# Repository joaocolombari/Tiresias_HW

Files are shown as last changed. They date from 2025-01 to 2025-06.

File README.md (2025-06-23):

<div align="center">
  <h1>Tiresias Hardware</h1>
   <p>Altium Designer Hardware files for the Tiresias Hearing Aid project </p>
</div>

<p align="center">
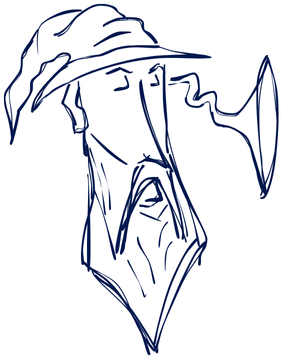
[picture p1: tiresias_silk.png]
  
</p>

<div align="center">
  
  
  
</div>

## Introduction

This repository contains the Altium Designer Project for the Tiresias Hearing Aid Development Board. 

The Tiresias project is part a partnership between the Brazilian Schools [FOB-USP](https://www1.fob.usp.br) and [EESC-USP](https://www.eesc.usp.br/) aiming to adress some of the Brazilian healthcare system's demands. Conduced by the [GMETA](https://sel.eesc.usp.br/jcarmo/metamaterials/) R&D Group, it aims to develop an open-source national technology for hearing aid applications using off-the-shelf components.

Tiresias is a low-power, resource-constrained open-source development board for hearing aid prototyping. It integrates an easy-to-program audio codec supporting both standard hearing aid functions — such as nonlinear amplitude compression and multichannel filtering — and advanced processing techniques, including adaptive filtering and beamforming for noise reduction and speech enhancement.

## System Architecture

### Key Features

- **Advanced Signal Processing**
  - Multichannel compression for improved speech intelligibility
  - Adaptive microphone directivity (beamforming, cardioid)
  - Noise reduction using directional microphone arrays

- **Wireless Connectivity & IoT Integration**
  - Bluetooth LE Audio (BT 5.4) with LC3 codec support
  - Isochronous Channels for synchronized, low-latency audio streaming
  - Support for binaural and Auracast™ systems
  - Remote configuration and smartphone/device interaction

- **Sensor Integration**
  - Voice Pick-Up Units (VPU): Bone-conduction speech capture for noisy environments
  - MEMS Microphones: Multi-microphone, low-power setups
  - Inertial Measurement Units (IMUs): Head tracking, ExG augmentation, fall detection, and health monitoring

- **Power Management**
  - Support for rechargeable Li-Po batteries
  - Power Management ICs (PMICs) for voltage regulation and safe charging

### Hardware overview

The project uses a [nRF5340 SoC](https://www.nordicsemi.com/Products/nRF5340) from [Nordic Semiconductors](https://www.nordicsemi.com). It contains an **application proccessor** for handling the main functions and a dedicated **network processor** for handling Bluetooth Low Energy (BLE) connectivity. Moreover, the design integrates:

- **[ADAU1787 Audio Codec](https://www.analog.com/en/products/adau1787.html)**  audio codec from [Analog Devices](https://www.analog.com/en/index.html) with integrated digital signal processing (DSP) instructions for real-time signal processing;
- Onboard **Nordic [nPM1100 PMIC](https://www.nordicsemi.com/Products/nPM1100)** battery management system for portable operation;
-  **Multiple [AMM-3742-T-WP-R MEMS microphones](https://puiaudio.com/product/microphones/amm-3742-t-wp-r)** from [PUI Audio](https://puiaudio.com/) for beamforming and noise reduction applications;
-  **[V2S200D](https://www.mouser.com/datasheet/2/218/v2s200d_user_guide-3179748.pdf) Digital Voice Vibration Sensor** from [Knowless](https://www.knowles.com/) for self-speech recognition and adaptation; 
-  **[BMI270[(https://www.bosch-sensortec.com/products/motion-sensors/imus/bmi270/) Inertial Measurement Unit** from [Bosch](https://www.bosch-sensortec.com/) for motion and physiological data monitoring;
-  **[MX25R1635](https://www.mxic.com.tw/zh-tw/flash-memory-solutions/automotive/Pages/spec.aspx?p=MX25R1635F&m=Automotive&n=PM2744) 16Mb Flash Memory** from [Macronix International{(https://www.mxic.com.tw/en-us/Pages/default.aspx);
- Versatile I/O interface for seamless development;
- Compact 40x25mm six-layer PCB for streamlined deployment.

<p align="center">
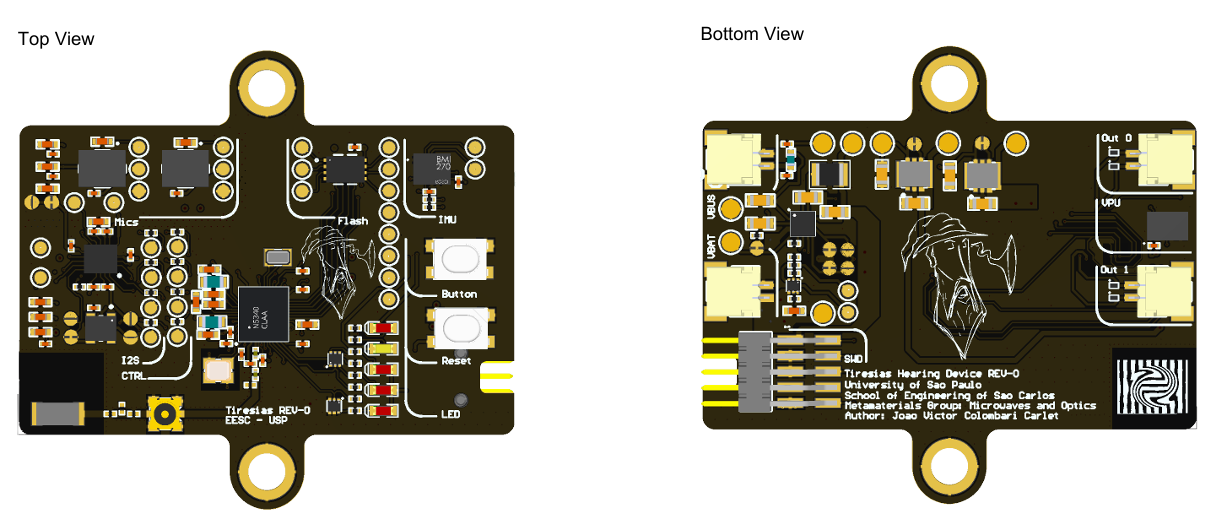
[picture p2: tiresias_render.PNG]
  
</p>

### Firmware overview

Firmware is available and documented in the [Tiresias Firmware Repo](https://github.com/felipepimentab/tiresias-fw).

## Usage 

<p align="center">
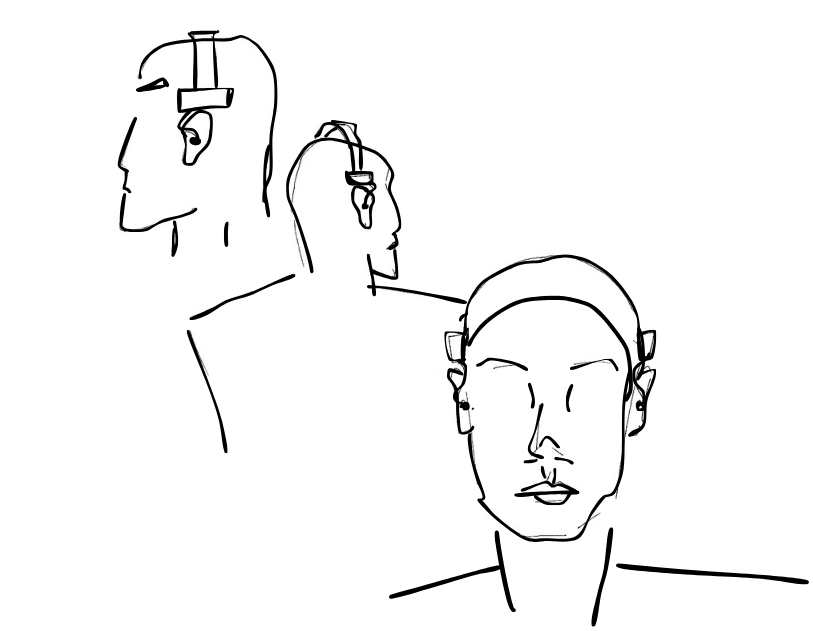
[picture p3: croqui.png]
  
</p>

### Target User

Tiresias can be applied in hearing aid **researchers and product developers**. It provides a flexible and accessible tool for researchers and innovators in the field of hearing solutions, as well as for consumer audio designers.

### How to use it

Tiresias is built using Nordic Semiconductor's **nRF Connect Software Development Kit (NCS)**, which integrates the **Zephyr Real-Time Operating System**. For the audio processing scheme on the DSP, Analog Devices offers the **SigmaStudio SDK** for its family of audio processors, which features a GUI that enables the user to configure fixed-function processors. In the firmware repository a Driver for the ADAU1787 has been developed so that the user can flash the application usign the nRF processor. 

Thus, **software-wize**, make shure you have:

- Nordic [nRF Connect SDK](https://www.nordicsemi.com/Products/Development-software/nRF-Connect-SDK/GetStarted#infotabs)
- Analog Devices [SigmaStudio](https://www.analog.com/en/resources/evaluation-hardware-and-software/embedded-development-software/ss_sigst_02.html)
- Firmware repository content 

Tiresias has no interfae microprocessor, so it is loaded uding its Serial Write Debug interface (10-pin, 1.27mm), which can be controlled using a Jlink programmer or another microprocessor acting as such (a nRF5340 in another DK, for instance). 

For its first version, we decided to use external speaker sets, so the user must have a balanced armature or an in-ear phone. A good setup for using it would be the one shown in the figure above, that holds a Tiresias PCB on each of the user's temples and connects them to in-ear phones. This will be soonly implemented and made publically available. 

So, **hardware-wize**:

- A Jlink debuger 
- Speakers of some kind

## Funding

To the present, this project has been completelly financed by the University of São Paulo.

## Acknowledgments

- **EESC-USP**: For providing the infrastructure and finantial support for this research.
- **Nordic Semiconductor**: For providing the nRF5340 Audio and nRF5340 Development Kits (DK) used in this project and extensive support.
- **Analog Devices**: For providing the ADAU1787 codec used in this project and extensive support.

## Contributors

<table>
  <tr>
    <td align="center">
      <a href="https://www.linkedin.com/in/joaocolombari/">
        Felipe Pimenta Bernardo on LinkedIn<br>
        <sub>
          <b>João Colombari</b>
        </sub>
      </a>
    </td>
    <td align="center">
      <a href="https://www.linkedin.com/in/felipepimentab/">
        João Colombari on LinkedIn<br>
        <sub>
          <b>Felipe Pimenta Bernardo</b>
        </sub>
      </a>
    </td>
    <td align="center">
      <a href="https://github.com/brunochenriques">
        Bruno Henriques on GitHub<br>
        <sub>
          <b>Bruno Henriques</b>
        </sub>
      </a>
    </td>
  </tr>
</table>

## Contact

Feel free to reach out through our LinkedIn profiles (linked above) or contact us directly via email:

- João Carlet – [jvccarlet@usp.br](mailto:jvccarlet@usp.br)

## 📝 License

This project is licensed under the **CERN Open Hardware License - Strongly Reciprocal (CERN OHL-S)**.

You may use, modify, and distribute the hardware and software covered by this license under the terms specified in the license.

### Summary of the CERN OHL-S:

- You are free to use, modify, and distribute the hardware and/or software, provided that any derivative works are also licensed under the **CERN OHL-S**.
- If you distribute modified versions of the hardware or software, you must make the modifications available under the same license, and the modified version must include a clear notice stating that it has been modified.
- This license includes a strong reciprocity requirement, meaning that if you use the design in a commercial product, you must make the corresponding source available.

For the full text of the license, please see the [LICENSE](LICENSE) file.

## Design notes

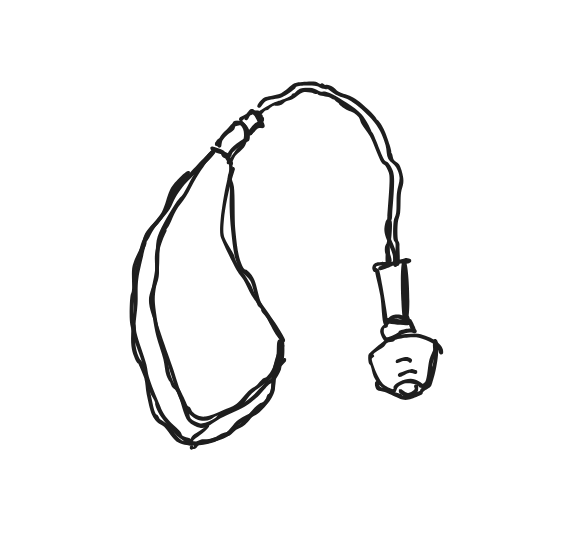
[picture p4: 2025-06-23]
Design sem nome-4.png

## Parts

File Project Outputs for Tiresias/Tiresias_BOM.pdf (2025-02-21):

Description | Value | Quantity | Designator | Manufacturer | Part Number
2.45 GHz chip antenna | 2450AT18B100 | 1 | A1 | Johanson Technology | Johanson 2450AT18B100
Microphones MICROPHONE -42 DB 2 VDC 200 UA 300 OHM,20 Hz ~ 20 kHz Analog Microphone MEMS (Silicon) 1.5 V ~ 3.6 V Omnidirectional (-42dB +/-1dB) Solder Pads | N.A. | 2 | B1, B2 | PUI Audio | AMM-3742-T-WP-R
IMUs - Inertial Measurement Units Smart Ultra-Low Power Inertial Measurement Unit (IMU) for Wearable Applications | | 1 | B3 | Bosch | BMI270
Capacitor, 0.7p, 0201, NP0, ±2% | 0.7p | 1 | C1 | N.A. | C0201-0p7
Capacitor, 1uF, 0402, X5R, ±5% | 1uF | 11 | C2, C3, C5, C7, C10, C14, C15, C32, C38, C40, C54 | N.A. | C0402-1µ0
Capacitor, 2.2nF, 0201, NP0, ±2% | 2.2nF | 1 | C4 | N.A. | C0201-2n2
Capacitor, 100nF, 0201, NP0, ±2% | 100nF | 23 | C6, C8, C9, C11, C12, C13, C16, C17, C21, C26, C27, C28, C29, C33, C34, C39, C41, C42, C44, C47, C48, C51, C53 | N.A. | C0201-100n
Capacitor, 10uF, 0402, X5R, ±5% | 10uF | 3 | C18, C20, C52 | N.A. | C0402-10µ
Capacitor, NC, 0201, NP0, ±2% | N.C. | 4 | C19, C35, C36, C37 | N.A. | C0201-NC
Capacitor, 2.2uF, 0603, Ceramic, X5R, ±10%, 10V | 2.2µF | 1 | C22 | N.A. | C0603-2µ2-10V-X5R
Capacitor, 10uF, 0603, X5R, ±10% | 10uF | 5 | C23, C24, C25, C30, C49 | N.A. | C0603-10µ
Capacitor, 22uF, 0603, X5R, ±20%, 6.3V | 22µF | 2 | C31, C50 | N.A. | C0603-22µ
Capacitor, 10nF, 0201, NP0, ±2% | 10nF | 1 | C43 | N.A. | C0201-10n
Capacitor, 1u5F, 0402, X5R, ±5% | 1u5F | 2 | C45, C46 | N.A. | C0402-1µ5
Very low capacitance bidirectional ESD protection diode | PESD5V0V1BDSF | 4 | D1, D2, D3, D4 | Nexperia | PESD5V0V1BDSF
Ferrite Bead, 120 Ohm @ 100MHz, 500mA, 250 mOhm Max | 120R/0.55A | 1 | FB1 | Murata | FB0402-120R@100M-500mA
General Purpose Audio Codec 4ADC / 2DAC Ch 42-Pin WLCSP T/R | N.A. | 1 | IC1 | Analog Devices | ADAU1787BCBZRL
Coaxial Connector with Switch | MM8130-2600 | 1 | J1 | Murata | MM8130-2600
1.0mm pitch connector side entry SMD | SM02B-SRSS-TB | 4 | J2, J3, J4, J5 | JST Sales America Inc. | SM03B-SRSS-TB
Inductor, 2.2nH, 0201 ±5%, High frequency | 2.2nH | 2 | L1, L2 | N.A. | L0201-2n2
Inductor, 10uH, 0603, IDC, min = 50 mA, ±20% | 10uH | 2 | L3, L4 | N.A. | L0603-10µ
Inductor, 2.2uH, 0806, 2.5A 87MOHM SMD | 2.2µH | 1 | L5 | Samsung Electro-Mechanics | CIGT201610EH2R2MN E
LED, SMD, 0603, RED | L0603R | 4 | LD1, LD2, LD3, LD5 | Multicomp | OVS-0608 RED
LED, SMD, 0603, Yellow | L0603Y | 1 | LD4 | Wurth Elektronik | 150060YS75000
Pin Header 2x5, 1.27mm (50mil), SMD, Keying Shroud Angular | Pin Header 2x5, 1.27mm Angular | 1 | P1 | W-CON | Pin Header 2x5 SMD, 1.27mm, KS
MOSFET, Dual N and P-Channel, 20V, 450mA/310mA, 990mOhm, 350mW | DMC2990UDJ | 1 | Q1 | Diodes Incorporated | DMC2990UDJ-7
MOSFET, Dual N-Channel, 20V, 240mA, 1050mOhm, 300mW | DMN26D0UDJ | 2 | Q2, Q3 | Diodes Incorporated | DMN26D0UDJ-7
Resistor, 1M, 0201, ±1%, 0.05W | 1M0 | 5 | R1, R5, R8, R10, R13 | N.A. | R0201-1M0
Resistor, 1.5M, 0201, ±1%, 0.05W | 1M5 | 1 | R2 | N.A. | R0201-1M5
Resistor, 6.8k, 0201, ±1%, 0.05W | 6K8 | 1 | R3 | N.A. | R0201-6k8
Resistor, 220k, 0201, ±1%, 0.05W | 220k | 1 | R4 | N.A. | R0201-220k
Resistor, 220R, 0201, ±1%, 0.05W | 220R | 3 | R6, R7, R12 | N.A. | R0201-220R
Resistor, 470R, 0201, ±1%, 0.05W | 470R | 2 | R9, R11 | N.A. | R0201-470R
Resistor, 10k, 0201, ±1%, 0.05W | 10k | 2 | R14, R15 | N.A. | R0201-10k
Resistor, 1.8k, 0201, ±1%, 0.05W | 1K8 | 2 | R16, R17 | N.A. | R0201-1k8

Resistor, 33R, 0201, ±1%, 0.05W | 33R | 8 | R18, R19, R20, R21, R22, R23, R24, R25 | N.A. | R0201-33R
Tactile Switch, SPNO, SMD, 160gf, 4.2x3.3x2.5mm | PB SW | 2 | SW1, SW2 | KLS | KLS7-TS3401-2.5-160R
Multi-protocol Bluetooth Low Energy, IEEE 802.15.4, ANT and 2.4GHz proprietary system-on-chip | N.A. | 1 | U1 | Nordic Semiconductors | nRF5340-CLAA
0.9V Ultra-Low Quiescent Current, Inductor Built-in Step-Down DC/DC Converter, CL-2025-03 | XCL232D091 | 1 | U2 | Torex Semiconductor | XCL232D091KR-G
1.8V, 200mA Inductor Built-in Step-Down “micro DC/DC” Converter | XCL210C18 | 1 | U3 | Torex Semiconductor | XCL210C181GR-G
Li-Ion/Li-Polymer USB battery charger with a high efficiency buck regulator | nPM1100-CAAAC0 | 1 | U4 | Nordic Semiconductor | nPM1100-CAAAC0
Wide Vcc Range 16M-BIT [x 1/x 2/x 4] CMOS MXSMIO (SERIAL MULTI I/O) FLASH MEMORY | N.A. | 1 | U5 | Macronix | MX25R1635FZUIL0
Voice Pickup Sensor | N.A. | 1 | U7 | Knowless | V2S200D-1-8
XTAL SMD 2016, 32MHz, Cl=8pF, Total Tol: ±40ppm | 32MHz | 1 | X1 | Golledge | XTAL_SMD2016_32MH z_8pF_General
XTAL SMD 2012, 32.768kHz, Cl=9pF, Total Tol: ±50ppm | 32.768kHz | 1 | X2 | Golledge | XTAL_SMD2012_32. 768kHz_9pF_General
Standard Clock Oscillators Oscillator 2520 4-SMD 24.576MHz +/-50ppm -40°C ~ 85°C CMOS 1.8V ~ 3.3V 24.576 MHz | | 1 | Y1 | Abracon | ASDMB-24.576MHZ-LC-T

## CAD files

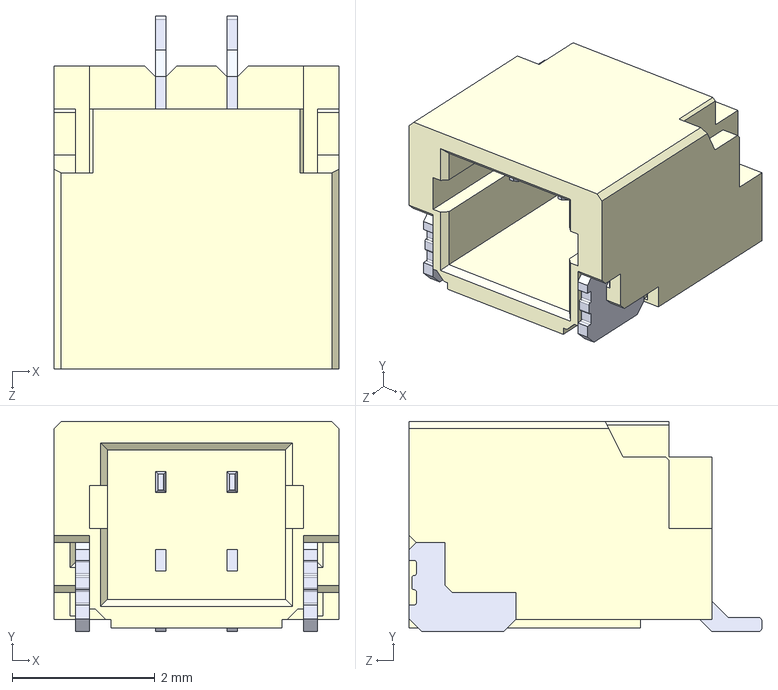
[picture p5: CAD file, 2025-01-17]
components/SM02B-SRSS-TB/SM02B-SRSS-TB-LF--SN---3DModel-STEP-56544.STEP
4.00 x 2.95 x 4.95 mm

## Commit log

2025-01-20 20/01 work
    [Tiresias.PrjPcb, Tiresias_Cover_letter.SchDoc, Tiresias_MCU.SchDoc, Tiresias_PMIC.SchDoc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]
2025-01-21 adau components disposed
    [Tiresias.PrjPcb, Tiresias_PMIC.SchDoc, Tiresias_active.SchLib, Tiresias_audio_codec.SchDoc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]
2025-01-22 22 - 01 work
    [SAMTEC_TSW-101-24-S-D.PcbLib, TSW-101-24-S-D.SchLib, TSW-101-24-S-D.stp, Tiresias_Cover_letter.SchDoc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]
2025-01-23 23 - 01 work
    [Tiresias_MCU.SchDoc, Tiresias_PMIC.SchDoc, Tiresias_mechanical.PcbLib, Tiresias_mechanical.SchLib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]
2025-01-24 work 24/01
    [Tiresias_audio_codec.SchDoc]
2025-01-27 work 27/01
    [Tiresias_mechanical.PcbLib, Tiresias_misc.SchDoc]
2025-01-28 work 28/01
    [Tiresias_MCU.SchDoc, Tiresias_audio_codec.SchDoc, Tiresias_misc.SchDoc]
2025-01-29 work 29/01
    [Tiresias.PrjPcb, Tiresias_MCU.SchDoc]
2025-01-31 PCB done
2025-01-31 outputs done
    [Tiresias.PrjPcb, Tiresias.xlsx, Tiresias_PCB.GBL, Tiresias_PCB.GBO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]
2025-02-07 Nordic revision
    [Tiresias.PrjPcb, Tiresias_PMIC.SchDoc]
2025-02-10 exported BOM
    [Tiresias.xlsx]
2025-02-12 error on MCU sheet text
    [Tiresias_MCU.SchDoc]
2025-02-13 added some test points, info on MCU sheet and regerenate outputs
    [Tiresias.PrjPcb, Tiresias_MCU.SchDoc, Tiresias_PCB.GBL, Tiresias_PCB.GBO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]
2025-02-21 fixing BOM
    [Tiresias_BOM.xlsx]
2025-03-24 pcb render
2025-06-23 added pullup on flash CS
    [Tiresias_misc.SchDoc]
2026-03-05 added 3D STEP in output files
    [Tiresias_PMIC.SchDoc, Tiresias_audio_codec.SchDoc]

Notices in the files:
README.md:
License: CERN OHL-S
